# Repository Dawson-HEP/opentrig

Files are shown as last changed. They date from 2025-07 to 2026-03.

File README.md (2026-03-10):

# opentrig

> ***open***-source ***trig***ger system

An open-source, integrated, particle physics data acquisition system (DAQ).

Designed to interface with timing systems controlled by the [AIDA-2020 TLU](https://gitlab.com/ohwr/project/fmc-mtlu).
Up to 24 digital trigger channels with variable-gain threshold setting.

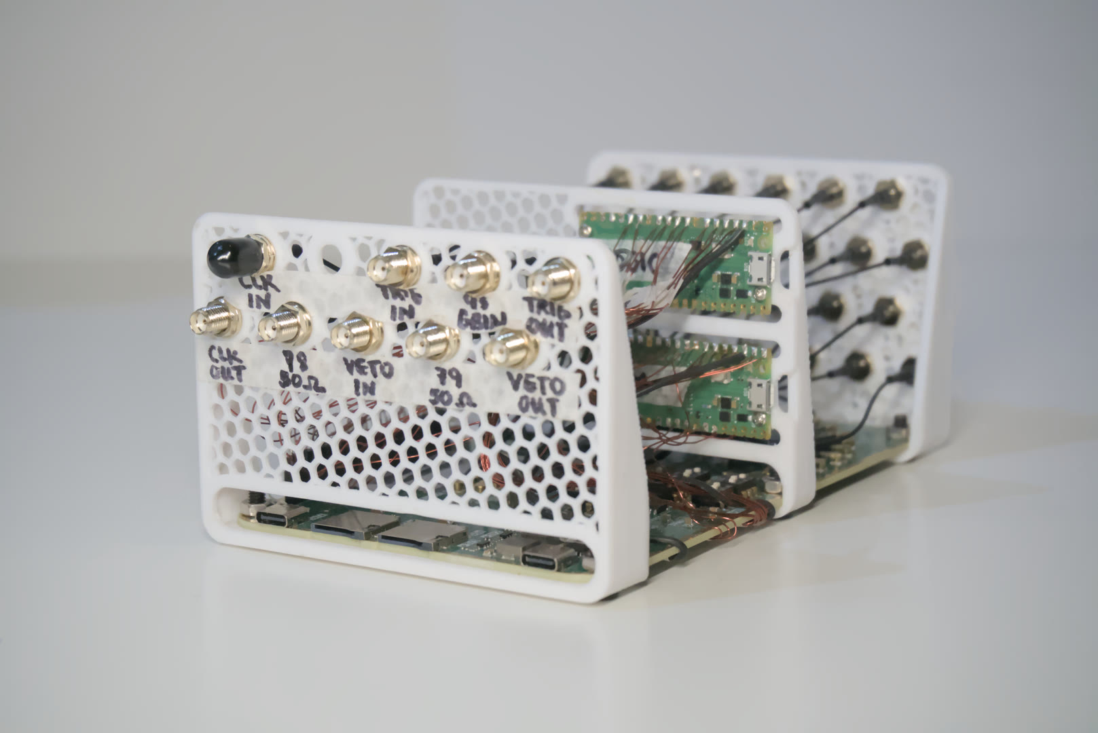
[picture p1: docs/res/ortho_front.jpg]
Main picture of opentrig


## Features

- 144 MHz internal FPGA clock, and timing resolution
- 24 digital trigger channels with variable gain
- Input voltage range 3.3V-5V
- TTL level compatible clock, trigger, input and output
- [AIDA-2020 TLU synchronous AIDA mode](https://gitlab.com/ohwr/project/fmc-mtlu/-/raw/master/Documentation/Main_TLU.pdf?ref_type=heads) (page 31) compatible FPGA

## Hardware Overview

[**Schematics can be found here.**](hardware/digital.pdf)

Front panel IO (left)
- Input clock signal (<40 MHz square wave)
- Output clock signal (120 MHz square wave, 3.3V TTL, <0.5% jitter, phase-locked)
- Input/output trigger (3.3V TTL)
- Input/output veto (3.3V TTL)
- Extra 50R impedance-matched inputs

Back panel (right)
- 24 channel digital inputs, with variable trigger thresholds (1.024 mV steps):
    - 0.000V-2.000V (1x gain)
    - 0.000V-4.000V (2x gain)

Internal components
- Low drift 5.000V reference (TI REF5050AIR)
- 12 high-speed thresholding comparators (TI TLV3502)
- 120 MHz MCU (RP2040)
- FPGA (Lattice ICE40 HX4K)

<p align="center">
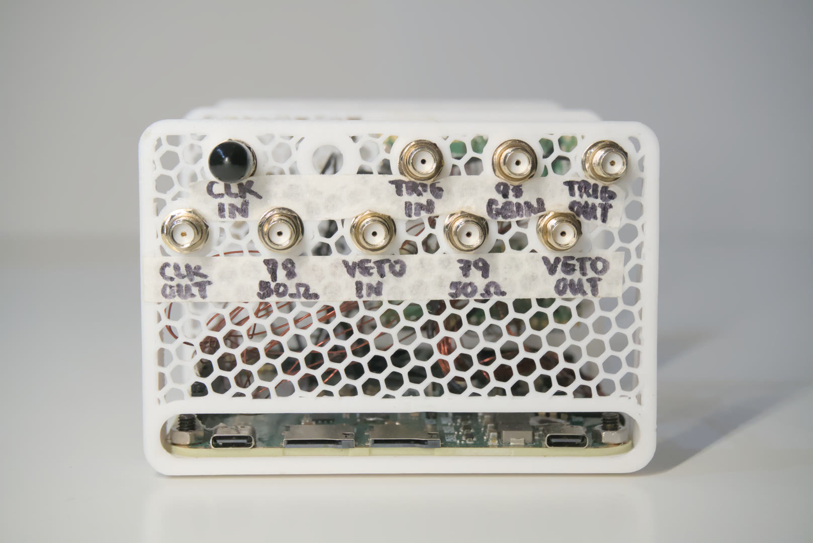
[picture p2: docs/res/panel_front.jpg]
Front panel
  
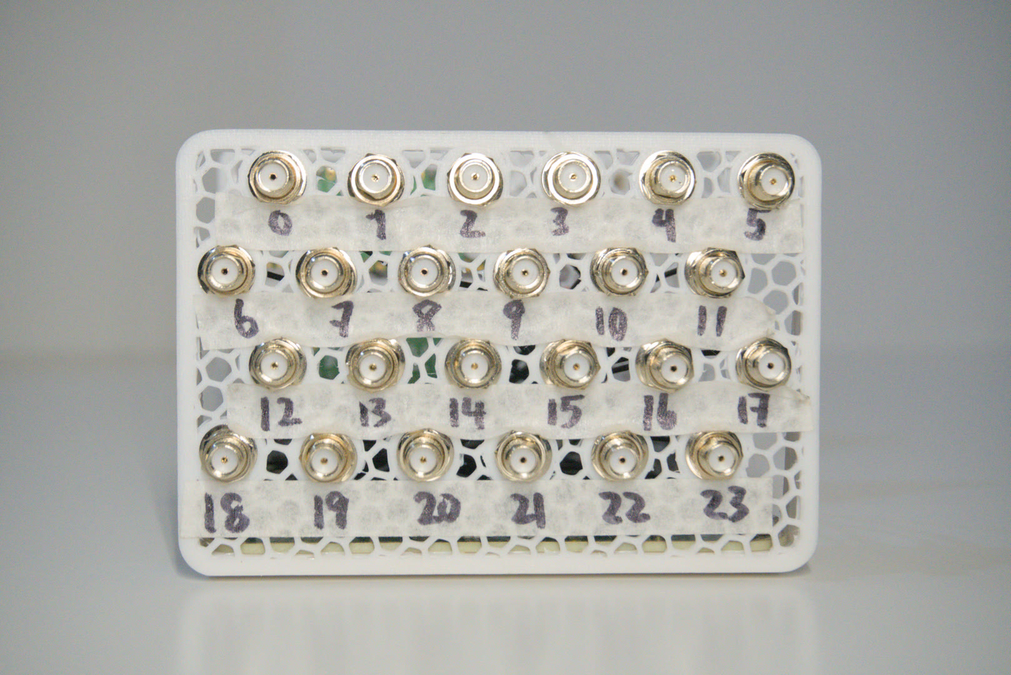
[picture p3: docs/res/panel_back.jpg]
Back panel
  
</p>

## Trigger Architecture

The *opentrig* system is a 24-channel, synchronous data acquisition platform compatible with EUDAQ2-compatible beamline trigger systems. Each channel digitizes an analog falling-edge into a digital rising-edge depending on a threshold set by independent digital-to-analog converters (DACs). Three trigger sources are fed into a selectable OR-ing gate, which allows for the selection of the interrupt source(s) for sample recording.

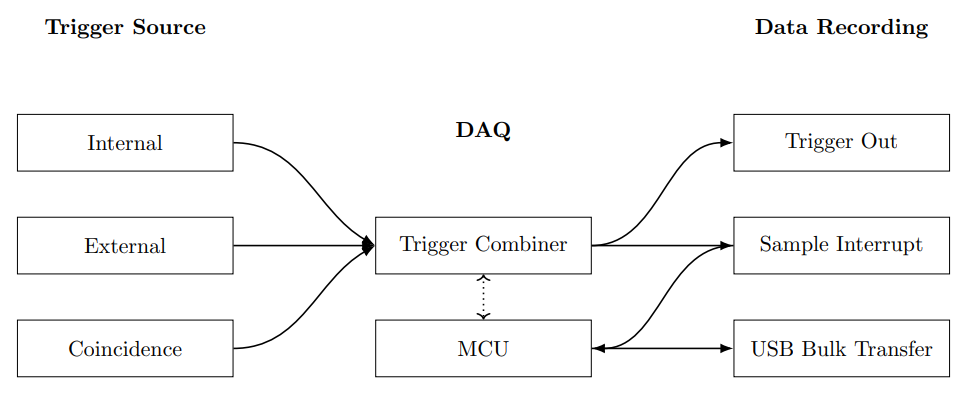
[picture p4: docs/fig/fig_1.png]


The trigger combiner vetoes priority in regards to the inputs of selected trigger sources, and assigns FPGA SPI bandwidth to the microcontroller (MCU) for processing and sampling. An active-high trigger output is asserted with controllable duration and delay in reference to the trigger sources. The sample interrupt interacts with the MCU in order to stream data live through the USB Type-C interface across bulk transfer.

### Trigger Delay

The delays incurred by the trigger is synchronized across channels by means of length matching. The largest skew is a result of level shifting: indeed up to $\pm 0.3$ ns across channels. No significant differences are measured in practice. FPGA gate skew is below the delays of level shifting, and are thus negligible in practice. PCB traces are delay-matched to within $\pm0.01$ mm. Given the assumption that channels are synchronized between each other, the input-output delay needs to be considered.

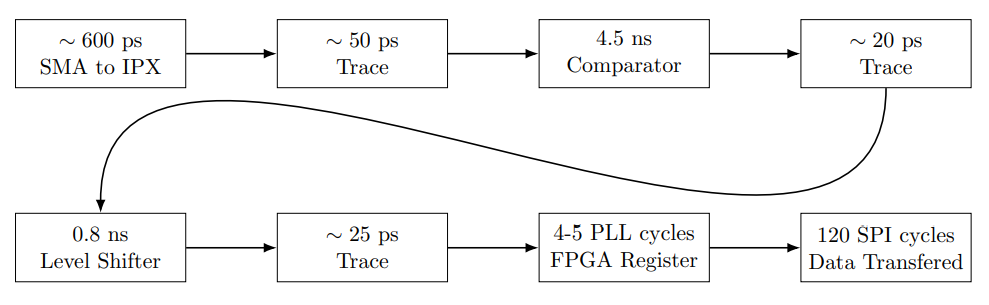
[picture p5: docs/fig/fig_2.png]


## Clocks

The FPGA PLL is synchronized to a sampling clock of $120$ MHz, while the SPI clock transfers data at a rate of $5$ MHz. The user can select an internal clock input or an external clock input, both requiring different PLL clock dividers to achieve the full sampling rate at $120$ Msps.

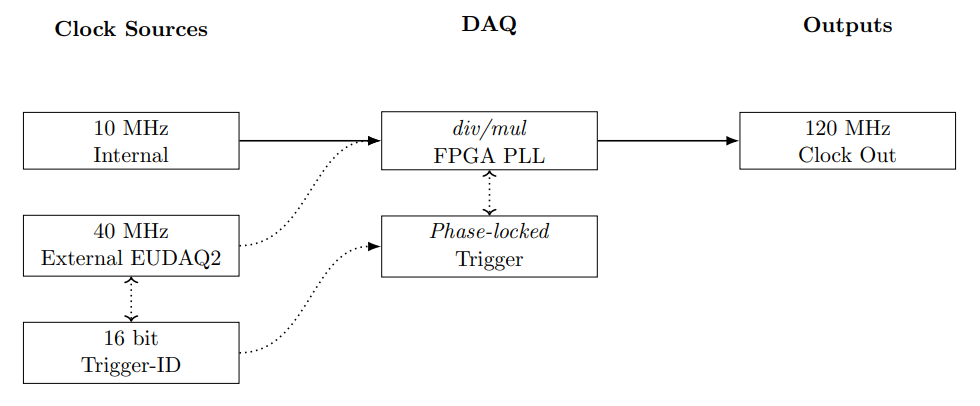
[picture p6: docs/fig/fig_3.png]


Clocks are phase-aligned by phase-locked-loop (PLL). An internal clock can be generated for the independent functioning of the DAQ. Proper PLL clock dividers and multipliers must be set to achieve the target $120$ MHz. An external clock compliant to EUDAQ2 trigger systems, such as the AIDA-2020 TLU, can be synchronized to \textit{opentrig}. A 16-bit trigger-ID can be read synchronously by the phase-locked external trigger module, which will be recorded upon the assertion of a sample interrupt.

## Voltage Levels

The 24 analog inputs are limited to a voltage range of $-0.30$ V to $+5.30$ V on wide-gain mode, and $-0.30$ V to $+3.30$ V on limited-gain mode. A voltage beyond permissible levels may cause irreversible damage to thresholding comparators, whose inputs are directly connected to SMA connectors.

The digital signals are high-impedance or $50 \Omega$ terminated depending on the label, and function on $3.3$ V CMOS voltage levels. The push-pull drivers have weak drive capabilities; therefore, only small digital loads may be attached with matched impedance.

## Directory Structure

The hardware is designed in [KiCad](https://www.kicad.org/) for the digital trigger front-end and mechanical layout, while the firmware and control utilities are written in [Rust](https://rust-lang.org/) using the [Embassy](https://embassy.dev/) embedded framework. The FPGA subsystems are written in pure Verilog with the [Yosys](https://github.com/YosysHQ/yosys.git) open-source toolchain, and [Project Icestorm](https://github.com/YosysHQ/icestorm)'s bitstream documentation.

```
opentrig/
├── hardware/ # KiCad hardware design
│   ├── fab/ # Fabrication files and gerbers
│   ├── logos.pretty/ # Custom logo footprints and graphics
│   └── digital.pretty/ # Custom digital footprints and component libraries
│
├── opentrig/ # Core DAQ firmware
│   ├── src/ # Source code (Rust + Embassy)
│   │   └── fpga/ # FPGA interface and logic modules
│   └── target/ # Compiled firmware output and build artifacts
│
├── cli/ # Command-line interface for control and configuration via host computer
│   ├── src/ # Rust source for CLI utilities
│   └── target/ # Compiled CLI binaries
│
├── tests/ # Automated and hardware-in-the-loop test framework
│   ├── src/ # Unit and integration test sources
│   └── target/ # Compiled test binaries and reports
│
└── README.md # Project overview, setup, and usage instructions
```

## Building

Before building the firmware and FPGA bitstream, you need to install a few dependencies for Rust and the FPGA toolchain. Follow these steps:

- Install [Rust](https://www.rust-lang.org/) – the firmware is written in Rust using the Embassy framework.
- Install [Just](https://github.com/casey/just) – used to run the build commands.
- Install [Yosys](https://github.com/YosysHQ/yosys) – for Verilog synthesis of the FPGA.
- Install [Project Icestorm](https://github.com/YosysHQ/icestorm) tools – for routing and bitstream generation for iCE40 FPGAs.
- Optional: [KiCad](https://www.kicad.org/) – for viewing and editing hardware schematics.

Once dependencies are installed, clone the repository, navigate to the firmware folder, and run the build commands:

```bash
# Clone the Protovolt repository from GitHub
git clone https://github.com/Dawson-HEP/opentrig.git

# Go to firmware directory
cd opentrig/opentrig
```

```bash
# Compile verilog bitstream
just build-verilog

# Compile embedded firmware
just build-rust
```

Flashing:
- SWD debug port on the PCB
- USB flashing via data port

## Running the DAQ
A USB Type-C Power Delivery (PD) supply must be connected to the power connector to bias analog and digital circuitry. A $100$ W-capable supply with $20$V output is preferred to provide enough margin for buck converters and analog filtering supplies to function properly. A digital data cable links the data acquisition computer with the DAQ.

## Debugging the DAQ
Three SWD debug interfaces are made available to the user: the main *opentrig* MCU debug link, the simulation PICO link, and the logic analyzer PICO link. The MCU flash process includes the FPGA bitstream, which is written upon power up of the DAQ. The simulation PICO, when powered, produce triggers via the internal links directly to the FPGA, which allows for programmatic debugging. The logic analyzer serves as a bitstream debugger, where internal registers and wires can be sampled.

## DESY Test Beam

The interfacing with the AIDA-2020 TLU functionality has been verified at the [DESY II Test Beam facility](https://desy.de/index_eng.html) in September of 2025, as part of the [Beamline for Schools](https://beamlineforschools.cern/) Competition. 

*Testbeam Area 21, Translation Stage*
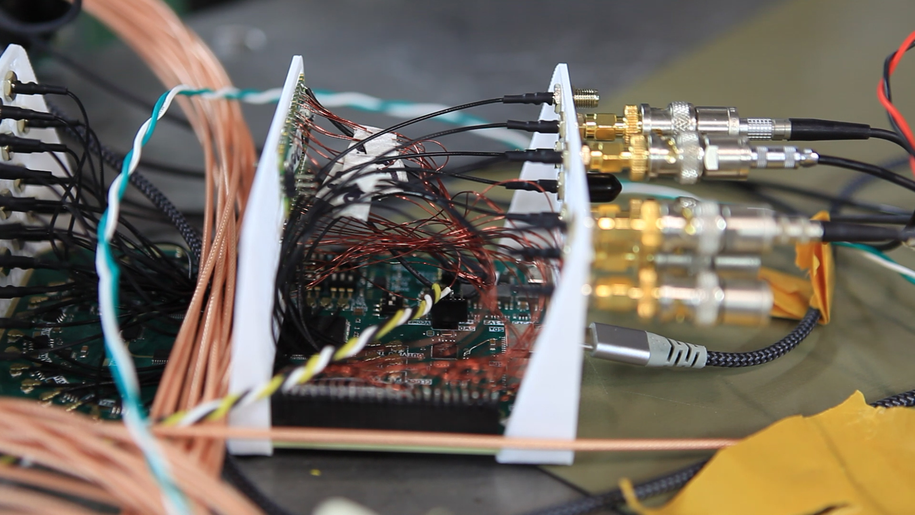
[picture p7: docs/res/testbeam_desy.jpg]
Testbeam


## Gallery

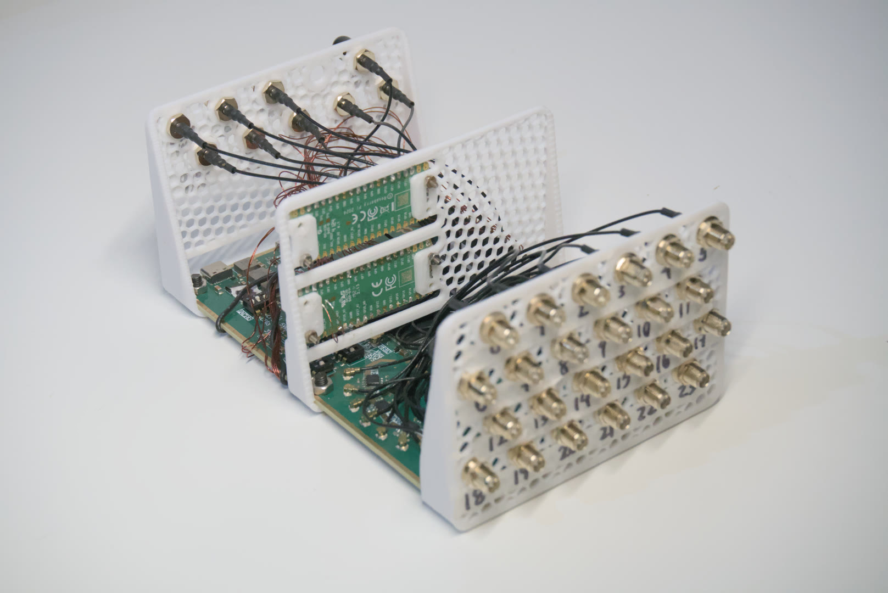
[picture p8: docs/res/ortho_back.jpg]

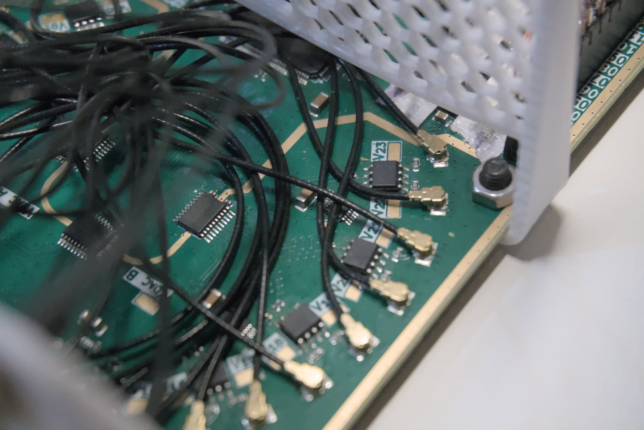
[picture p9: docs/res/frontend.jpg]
Frontend

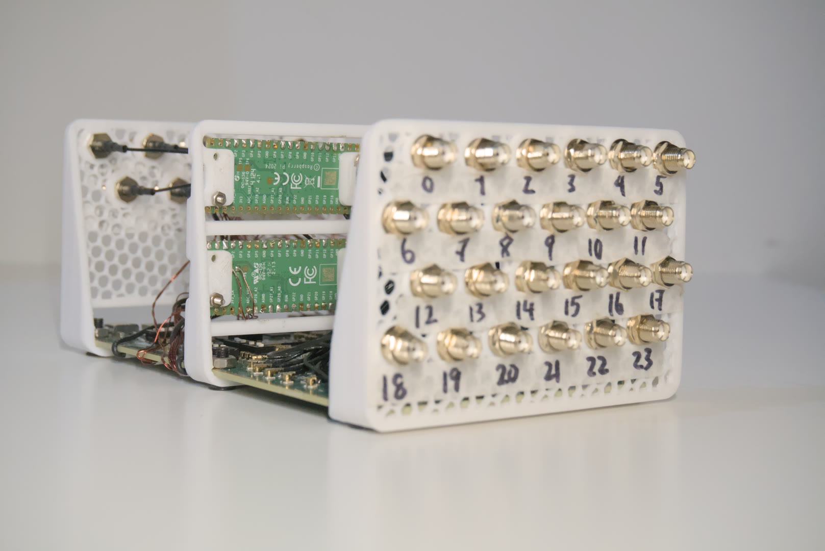
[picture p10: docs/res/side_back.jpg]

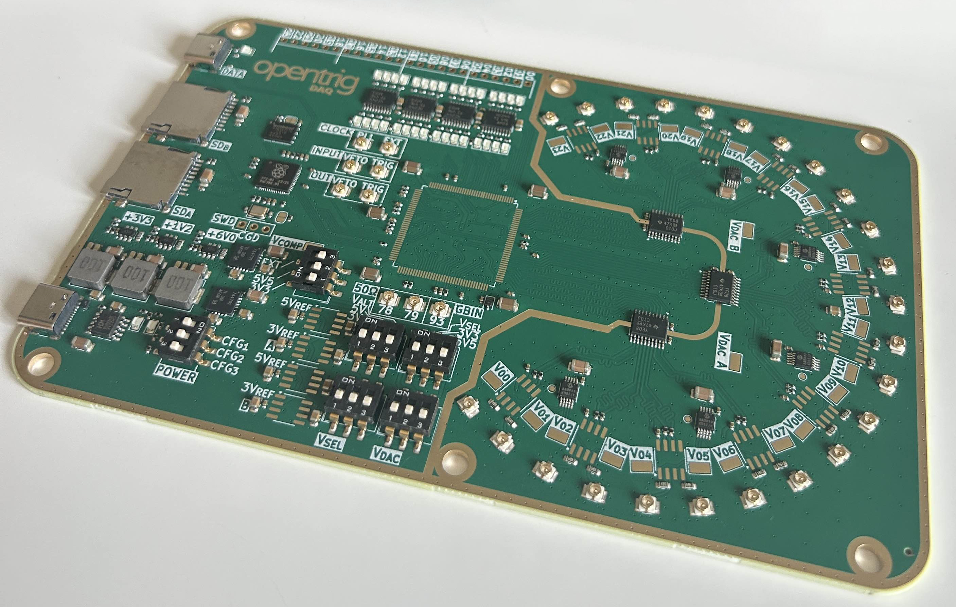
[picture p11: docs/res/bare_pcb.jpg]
Bare PCB


## License

This project is open-source under the Eclipse Public License - v 2.0.

## Authors

- [Tian Yi, Xia](https://github.com/ThatAquarel), xtxiatianyi@gmail.com
- [Leandro Perez-Moran](https://github.com/LudioRex), pemle2007@gmail.com

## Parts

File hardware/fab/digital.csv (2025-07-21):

Comment | Designator | Footprint | LCSC
100n | C1,C3,C4,C5,C6,C7,C8,C9,C11,C12,C13,C14,C15,C17,C19,C21,C22,C24,C25,C26,C27,C28,C29,C30,C31,C32,C36,C38,C41,C43,C51,C55,C59,C61,C69,C71,C73,C74,C77,C80,C81,C85,C86,C89,C92,C93,C97,C98,C99,C100,C101,C102,C103,C104,C105,C106,C107,C108,C109,C110,C111,C113,C114,C115,C116 | Capacitor_SMD:C_0402_1005Metric | C307331
1u | C10,C47,C48,C52,C53,C66,C67,C68,C70,C72,C75,C78,C82,C83,C87,C90,C94,C95,C112 | Capacitor_SMD:C_0805_2012Metric | C28323
4.7u | C2,C16,C18,C20,C23 | Capacitor_SMD:C_1206_3216Metric | C29823
1u 25V | C33,C34 | Capacitor_SMD:C_0402_1005Metric | C52923
10u | C35,C37,C42,C49,C50,C54,C60,C65,C76,C79,C84,C88,C91,C96 | Capacitor_SMD:C_1206_3216Metric | C13585
15p | C39,C40 | Capacitor_SMD:C_0402_1005Metric | C1548
100p | C44 | Capacitor_SMD:C_0402_1005Metric | C1546
22u | C45,C46,C57,C58,C63,C64 | Capacitor_SMD:C_0603_1608Metric | C60077
47p | C56,C62 | Capacitor_SMD:C_0402_1005Metric | C1567
LED | D1,D2,D3,D4,D5,D6,D8,D9,D11,D12,D13,D14,D15,D16,D17,D18,D19,D20,D21,D22,D23,D24,D25,D26,D27,D28,D29,D30,D31,D32,D33,D34,D35,D36,D37 | LED_SMD:LED_0805_2012Metric | C2297
ESDA25P35 | D10 | digital:D_1610_4027Metric | C1974707
1N4148WS | D7 | Diode_SMD:D_SOD-323 | C2128
IPEX-1 | J1,J2,J3,J4,J5,J6,J7,J8,J9,J21,J22,J23,J24,J25,J26,J27,J28,J29,J30,J31,J32,J33,J34,J35,J36,J37,J38,J39,J40,J41,J42,J43,J44 | digital:BWIPX-1-001E | C496552
Conn_01x03_Pin | J10,J11,J13,J15 | Connector_PinHeader_1.00mm:PinHeader_1x03_P1.00mm_Vertical_SMD_Pin1Left
Conn_01x10_Pin | J12 | Connector_PinHeader_1.00mm:PinHeader_1x10_P1.00mm_Vertical_SMD_Pin1Left
Conn_01x02_Pin | J14 | Connector_PinHeader_1.00mm:PinHeader_1x02_P1.00mm_Vertical_SMD_Pin1Left
Micro_SD_Card_Det1 | J16,J18 | digital:microSD_HC_MSD-4-A | C91145
Conn_01x03_Pin | J17 | Connector_PinHeader_2.54mm:PinHeader_1x03_P2.54mm_Vertical
USB_C_Receptacle_USB2.0_16P | J19,J20 | Connector_USB:USB_C_Receptacle_GCT_USB4105-xx-A_16P_TopMnt_Horizontal | C165948
Conn_01x24_Pin | J45 | Connector_PinHeader_2.54mm:PinHeader_1x24_P2.54mm_Vertical
10uH | L1,L2,L3 | Inductor_SMD:L_Changjiang_FXL0630 | C167223
49.9R | R1,R2 | Resistor_SMD:R_0402_1005Metric | C25120
470R | R10,R11,R12,R13,R14,R15,R16,R18,R58,R61,R62,R63,R64,R65,R66,R67,R68,R70,R71,R72,R73,R74,R75,R76,R77,R80,R81,R82,R83,R84,R85,R86,R87 | Resistor_SMD:R_0402_1005Metric | C25117
100R | R17 | Resistor_SMD:R_0402_1005Metric | C25076
10k | R21,R28,R29,R30,R31,R32,R34,R35,R48,R51,R55,R56,R57 | Resistor_SMD:R_0402_1005Metric | C25744
4.7k | R22,R23 | Resistor_SMD:R_0402_1005Metric | C25900
1k | R24,R27,R37,R50,R52,R54 | Resistor_SMD:R_0402_1005Metric | C11702
27R | R25,R26 | Resistor_SMD:R_0402_1005Metric | C138021
0R | R3,R4,R5,R6,R7,R8,R9,R19,R20,R33,R36,R69,R78,R88 | Resistor_SMD:R_0402_1005Metric | C17168
47k | R38,R40,R49 | Resistor_SMD:R_0402_1005Metric | C25792
100k | R39,R43 | Resistor_SMD:R_0603_1608Metric | C25803
33k | R41,R45 | Resistor_SMD:R_0402_1005Metric | C25779
100k | R42,R46 | Resistor_SMD:R_0402_1005Metric | C25741
22k | R44,R53 | Resistor_SMD:R_0402_1005Metric | C25768
220k | R47 | Resistor_SMD:R_0603_1608Metric | C22961
5.1k | R59,R60 | Resistor_SMD:R_0402_1005Metric | C25905
49.9R | R89,R90,R96,R97,R101,R102,R103,R104,R107,R108,R114,R115,R117,R118,R119,R120,R124,R125,R131,R132,R133,R134,R135,R136 | Resistor_SMD:R_0603_1608Metric | C23185
10R | R91,R92,R93,R94,R95,R98,R99,R100,R105,R106,R109,R110,R111,R112,R113,R116,R121,R122,R123,R126,R127,R128,R129,R130 | Resistor_SMD:R_0402_1005Metric | C25077
SW_DIP_x03 | SW1,SW2,SW3,SW4,SW5,SW6 | Button_Switch_SMD:SW_DIP_SPSTx03_Slide_6.7x9.18mm_W8.61mm_P2.54mm_LowProfile | C129079
TestPoint | TP1,TP2,TP3,TP5,TP6,TP11,TP14,TP16,TP18,TP23,TP25,TP27,TP31,TP34,TP36,TP38,TP43,TP45,TP46 | TestPoint:TestPoint_Pad_D1.0mm
TestPoint_Alt | TP4,TP7,TP8,TP9,TP10,TP12,TP13,TP15,TP17,TP19,TP20,TP21,TP22,TP24,TP26,TP28,TP29,TP30,TP32,TP33,TP35,TP37,TP39,TP40,TP41,TP42,TP44 | digital:TestPoint_Keystone_5015_Micro_Mini | C159868
ICE40HX4K-TQ144 | U1 | Package_QFP:TQFP-144_20x20mm_P0.5mm
CH224K | U10 | Package_SO:SSOP-10-1EP_3.9x4.9mm_P1mm_EP2.1x3.3mm | C970725
REF5030ID | U14,U19 | Package_SO:SOIC-8_3.9x4.9mm_P1.27mm | C2878155
MCP4728 | U15,U16,U18,U20,U21,U23 | Package_SO:MSOP-10_3x3mm_P0.5mm | C108207
REF5050ID | U17,U22 | Package_SO:SOIC-8_3.9x4.9mm_P1.27mm
74HC244 | U2,U11,U12,U13 | Package_SO:TSSOP-20_4.4x6.5mm_P0.65mm | C6835
TXB0108PW | U24,U29,U34 | Package_SO:TSSOP-20_4.4x6.5mm_P0.65mm | C53406
TLV3502AIDR | U25,U26,U27,U28,U30,U31,U32,U33,U35,U36,U37,U38 | Package_SO:SOIC-8_3.9x4.9mm_P1.27mm
W25Q32JVZP | U3 | Package_SON:WSON-8-1EP_6x5mm_P1.27mm_EP3.4x4.3mm | C571260
RP2040 | U4 | Package_DFN_QFN:QFN-56-1EP_7x7mm_P0.4mm_EP3.2x3.2mm | C2040
TPS54302 | U5,U8,U9 | Package_TO_SOT_SMD:SOT-23-6 | C129370
TPS7A4701 | U6,U7 | Package_DFN_QFN:Texas_RGW0020A_VQFN-20-1EP_5x5mm_P0.65mm_EP3.15x3.15mm_ThermalVias | C90084
12 MHz ABM8-272-T3 | Y1 | Crystal:Crystal_SMD_Abracon_ABM8AIG-4Pin_3.2x2.5mm | C20625731

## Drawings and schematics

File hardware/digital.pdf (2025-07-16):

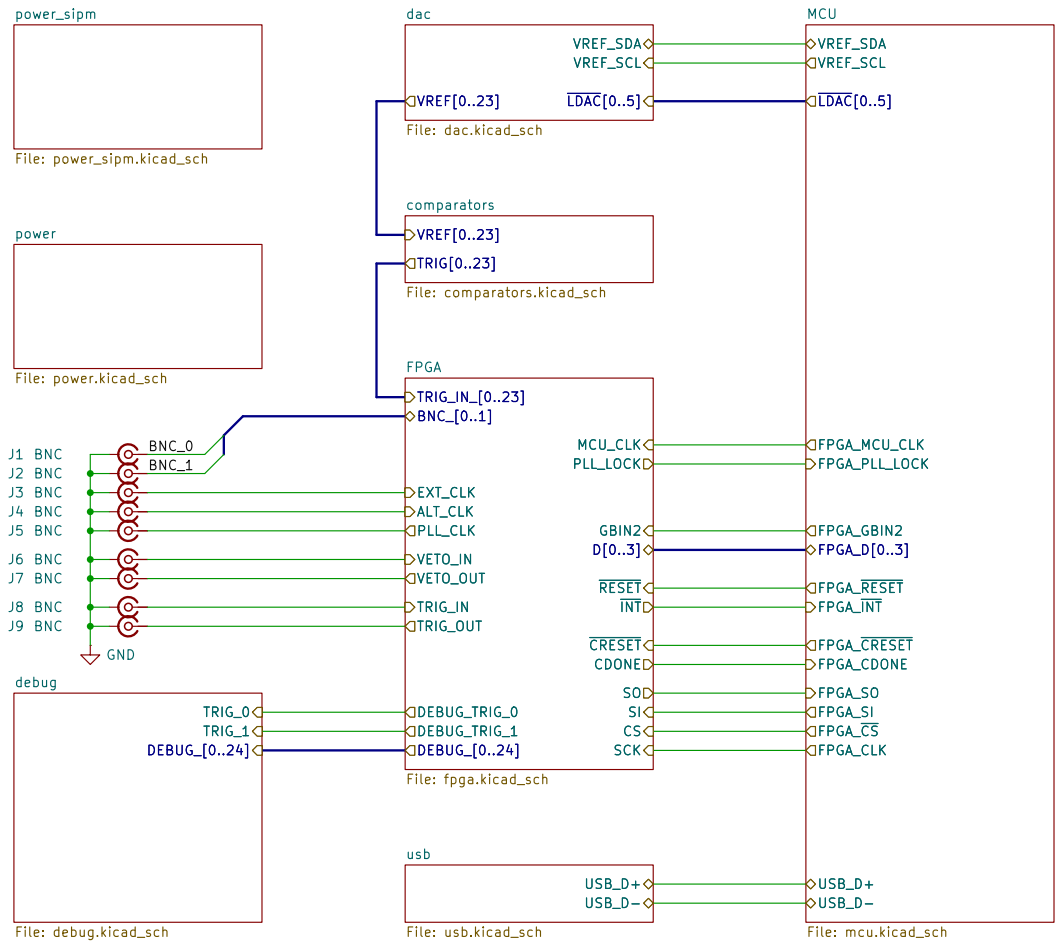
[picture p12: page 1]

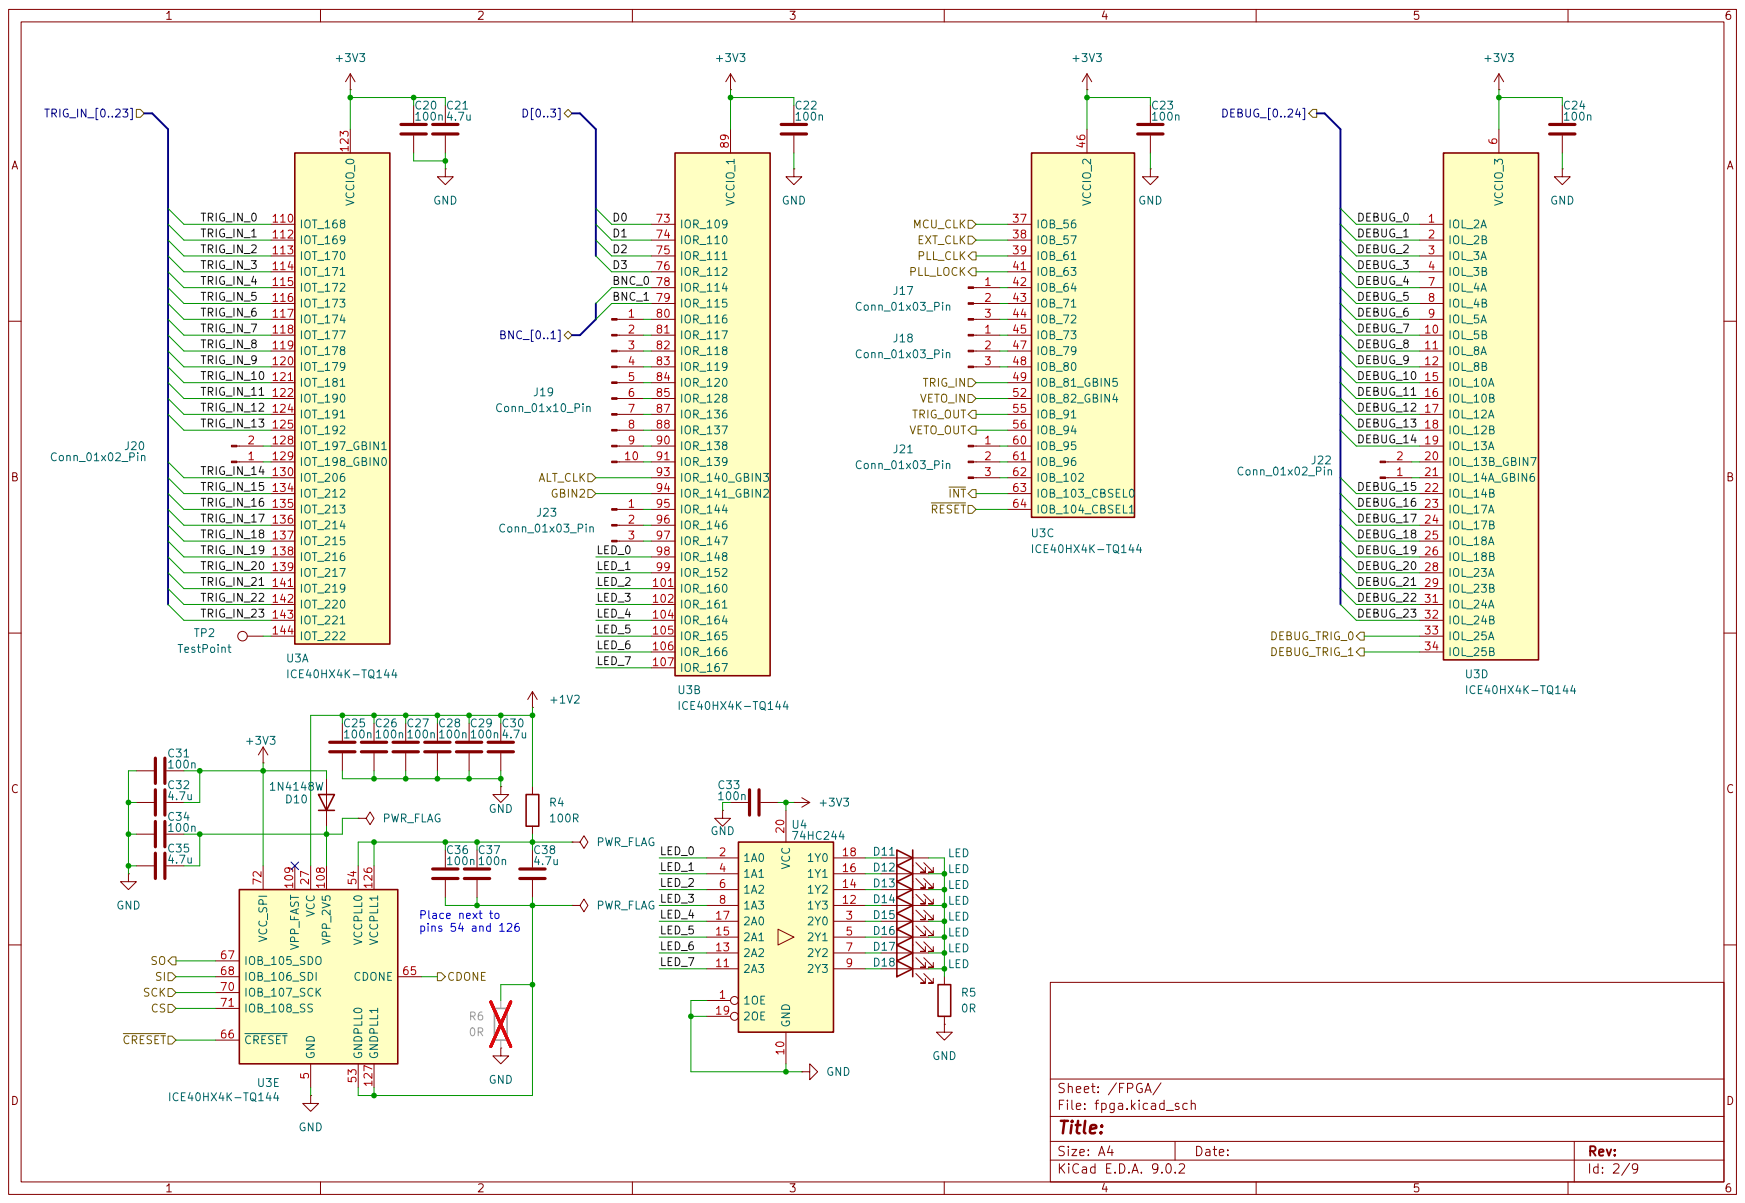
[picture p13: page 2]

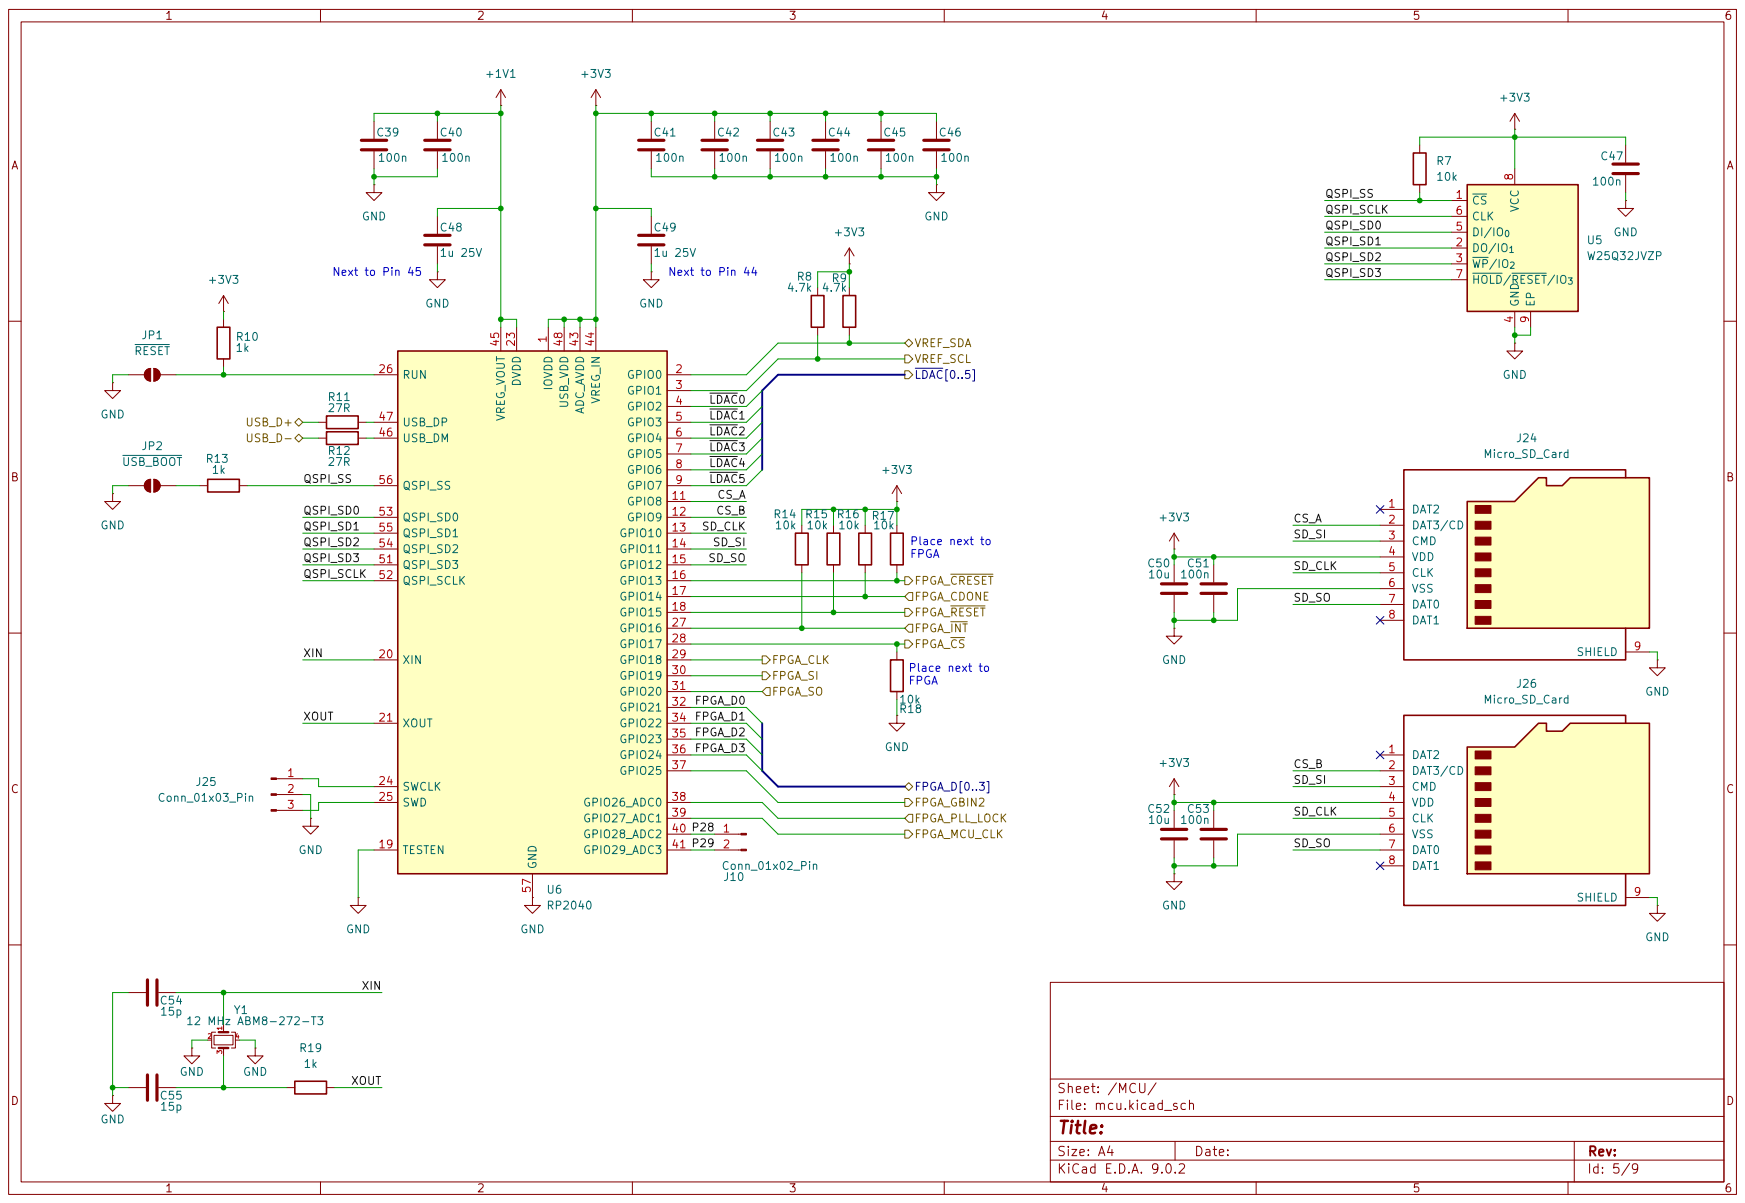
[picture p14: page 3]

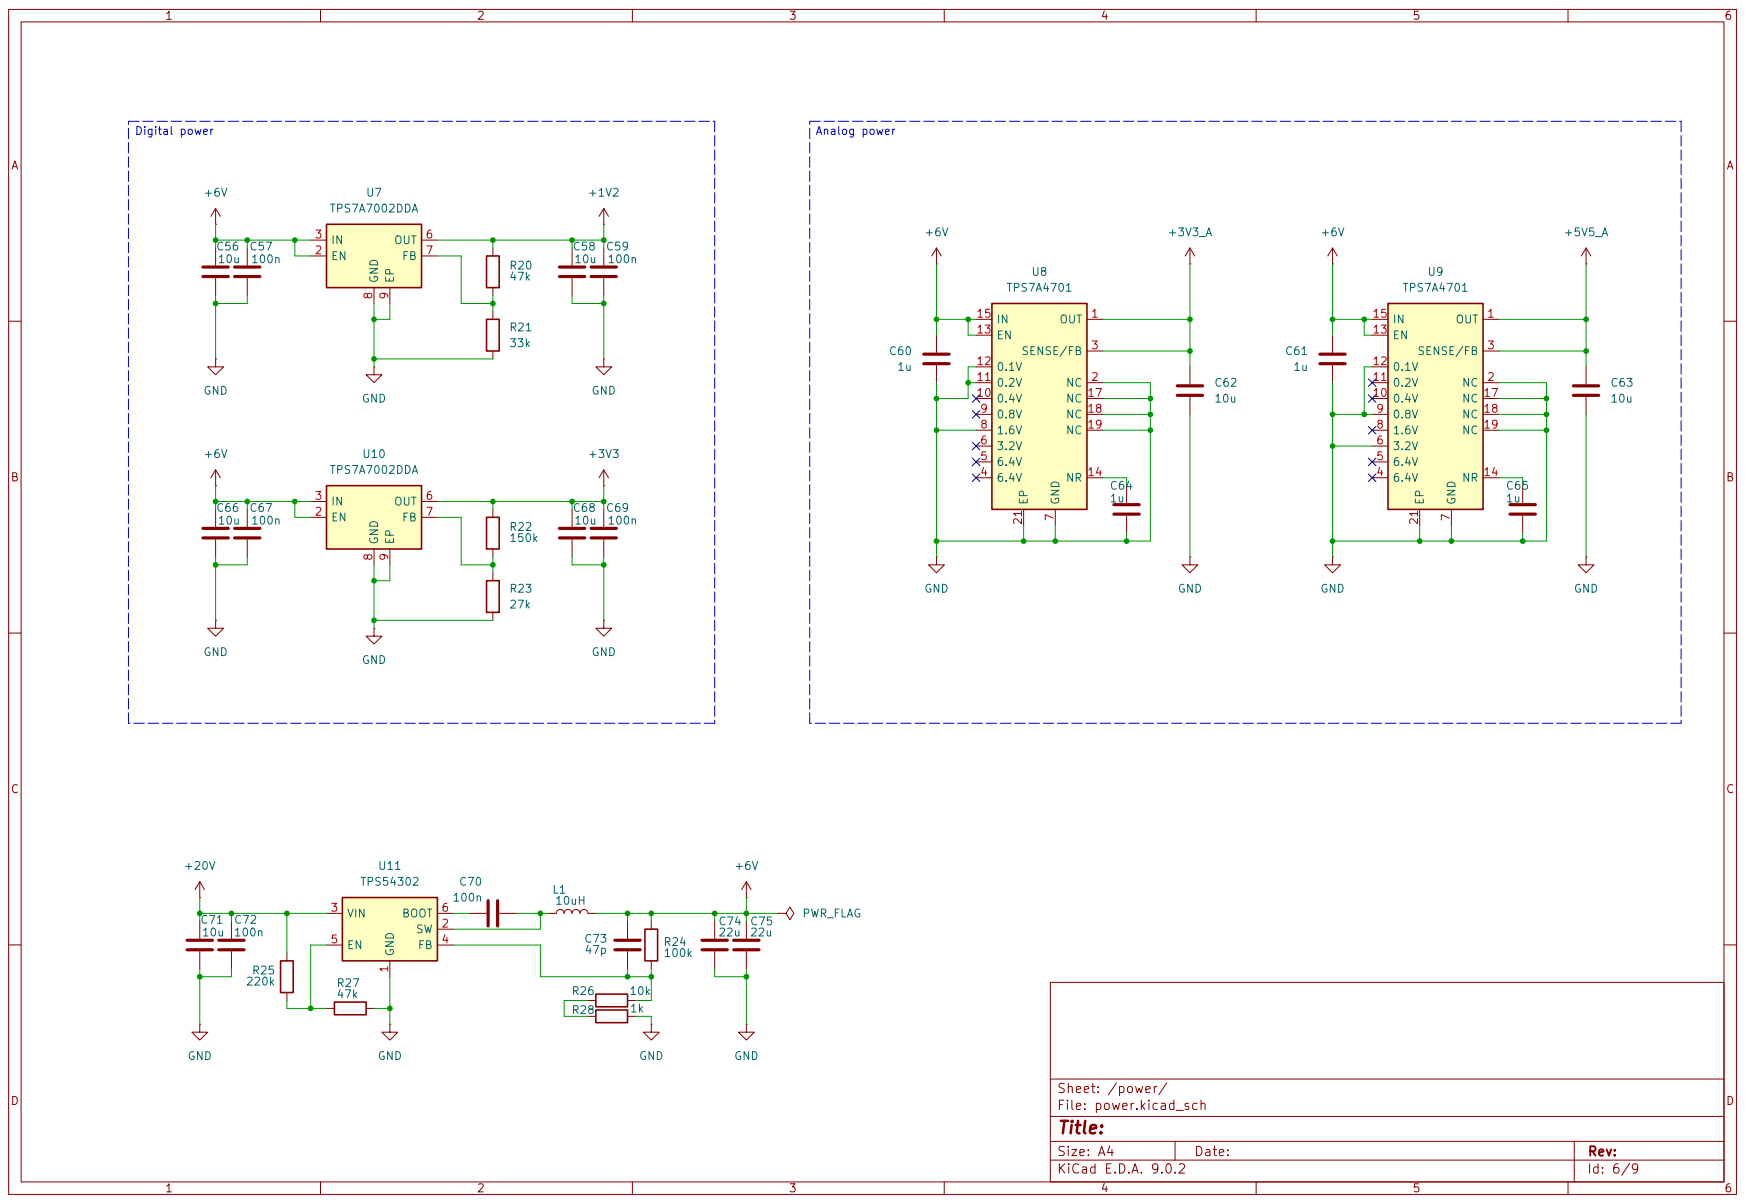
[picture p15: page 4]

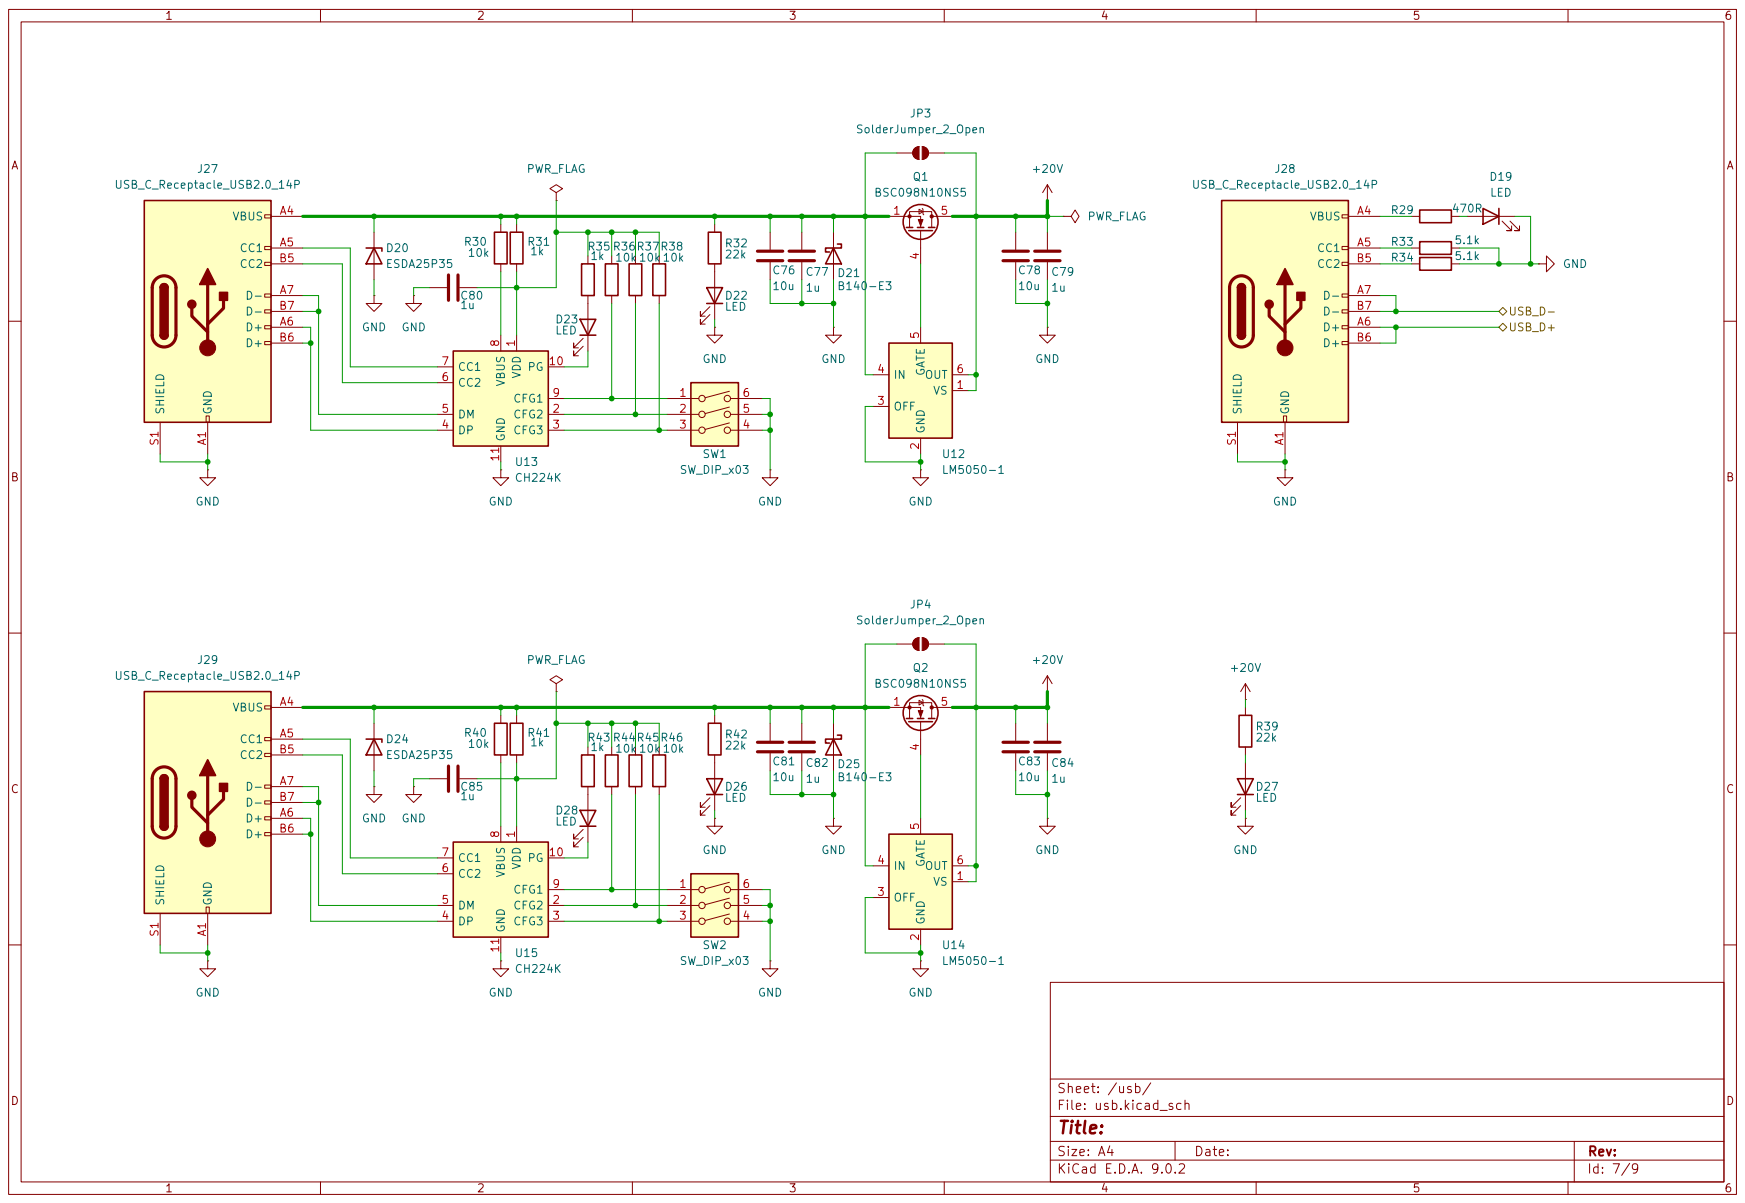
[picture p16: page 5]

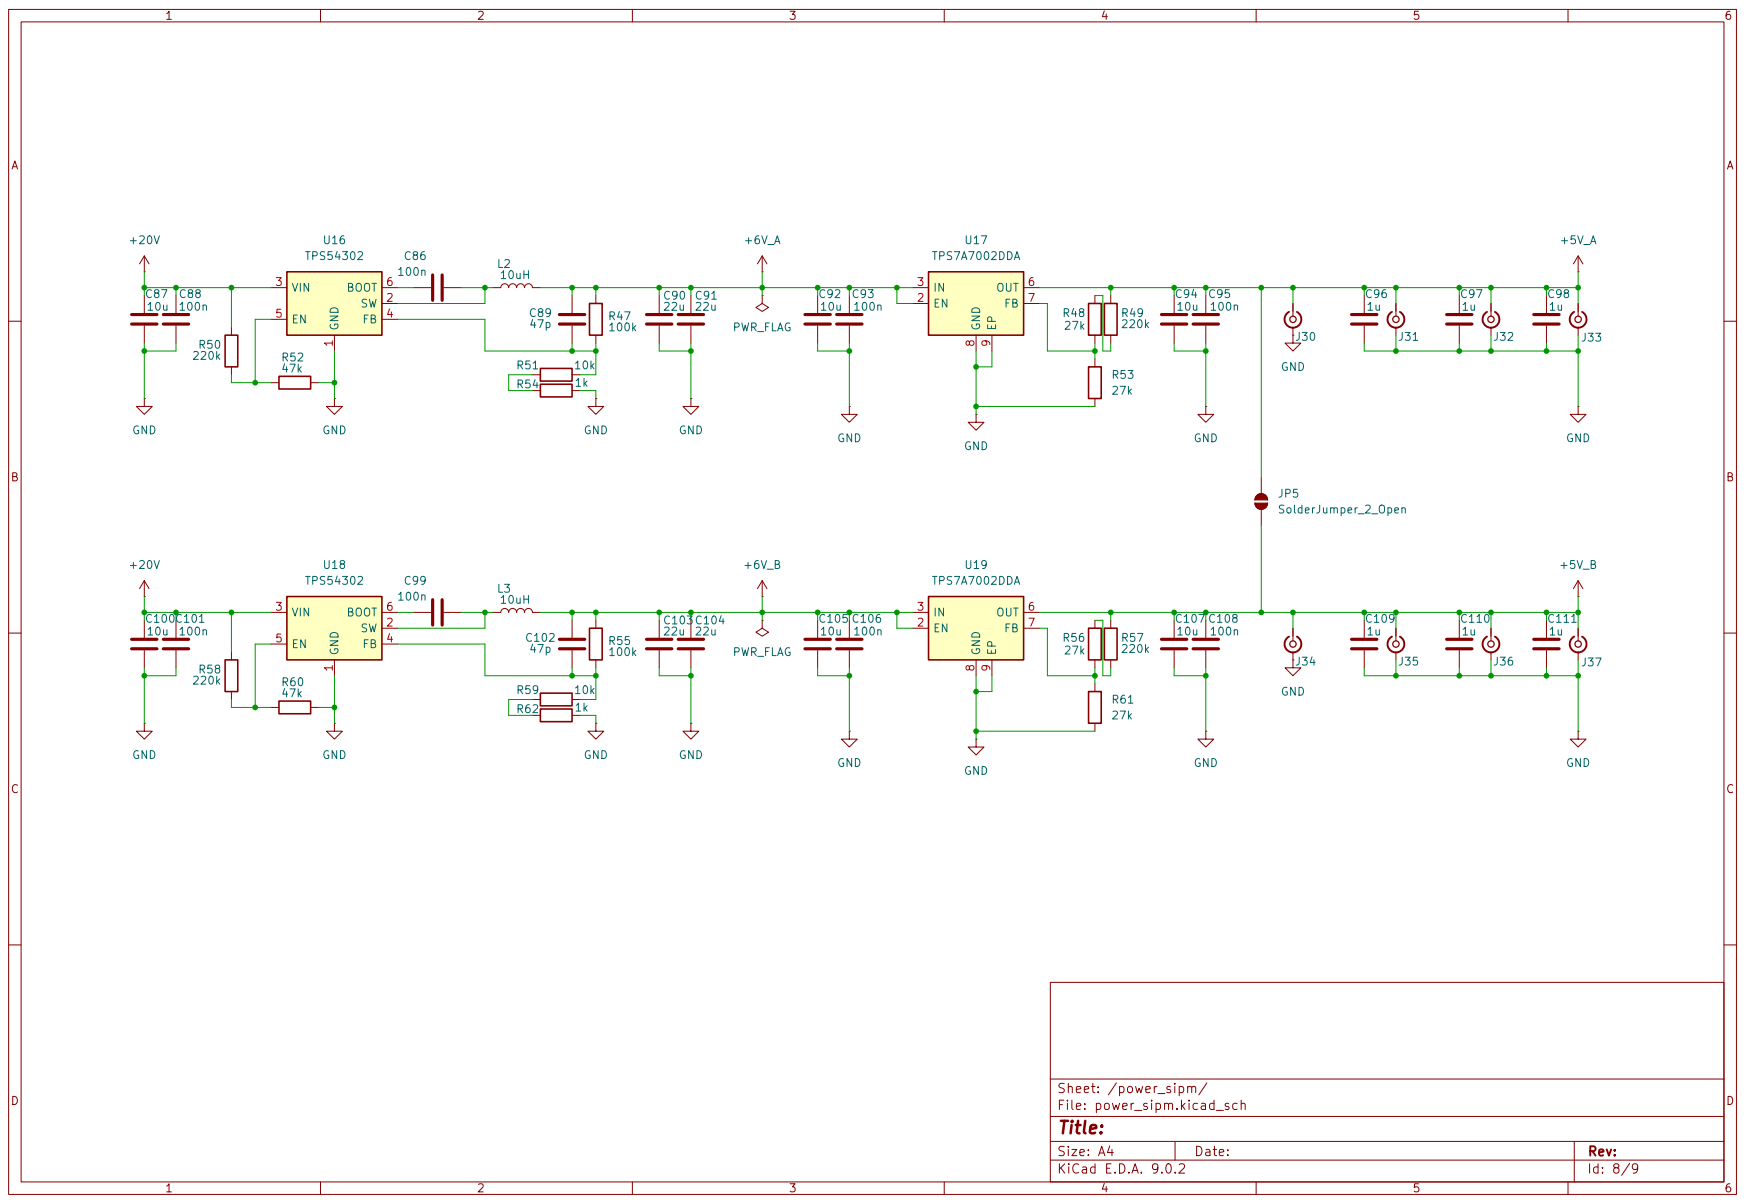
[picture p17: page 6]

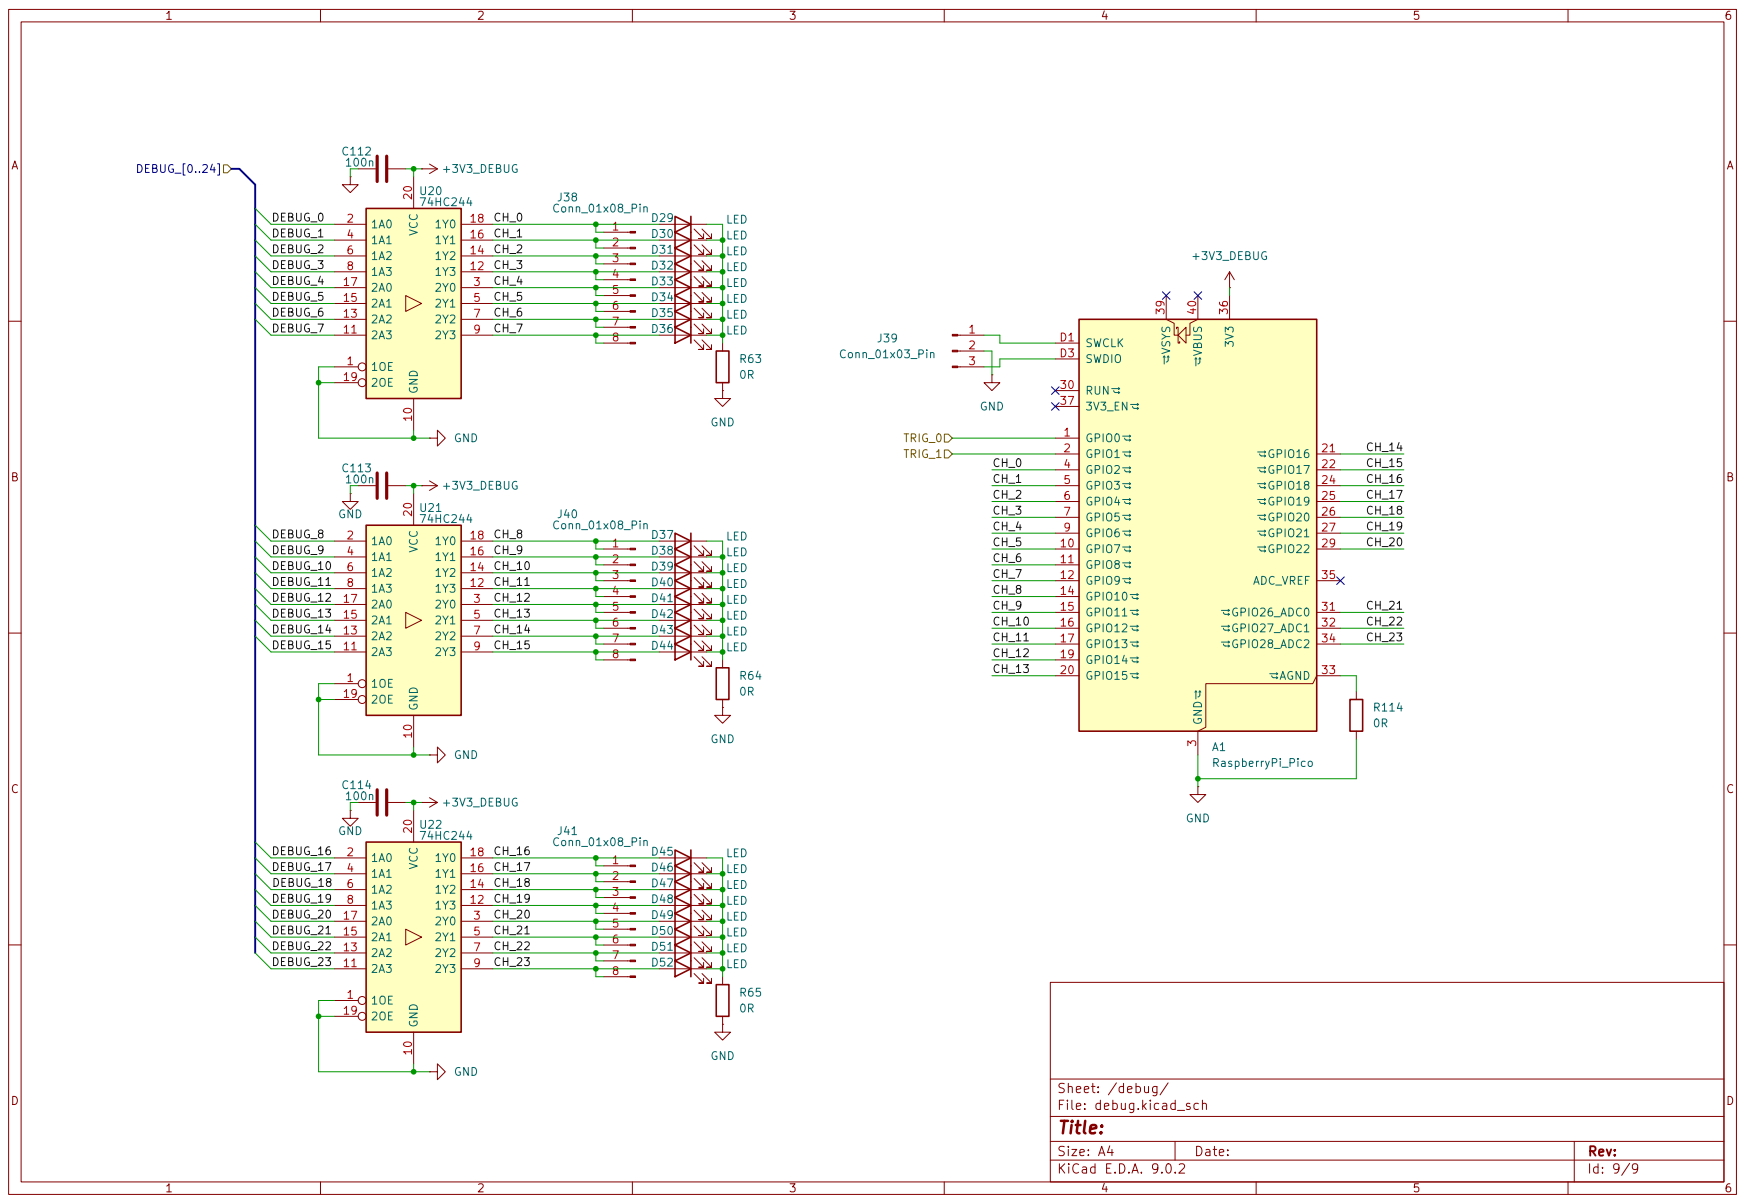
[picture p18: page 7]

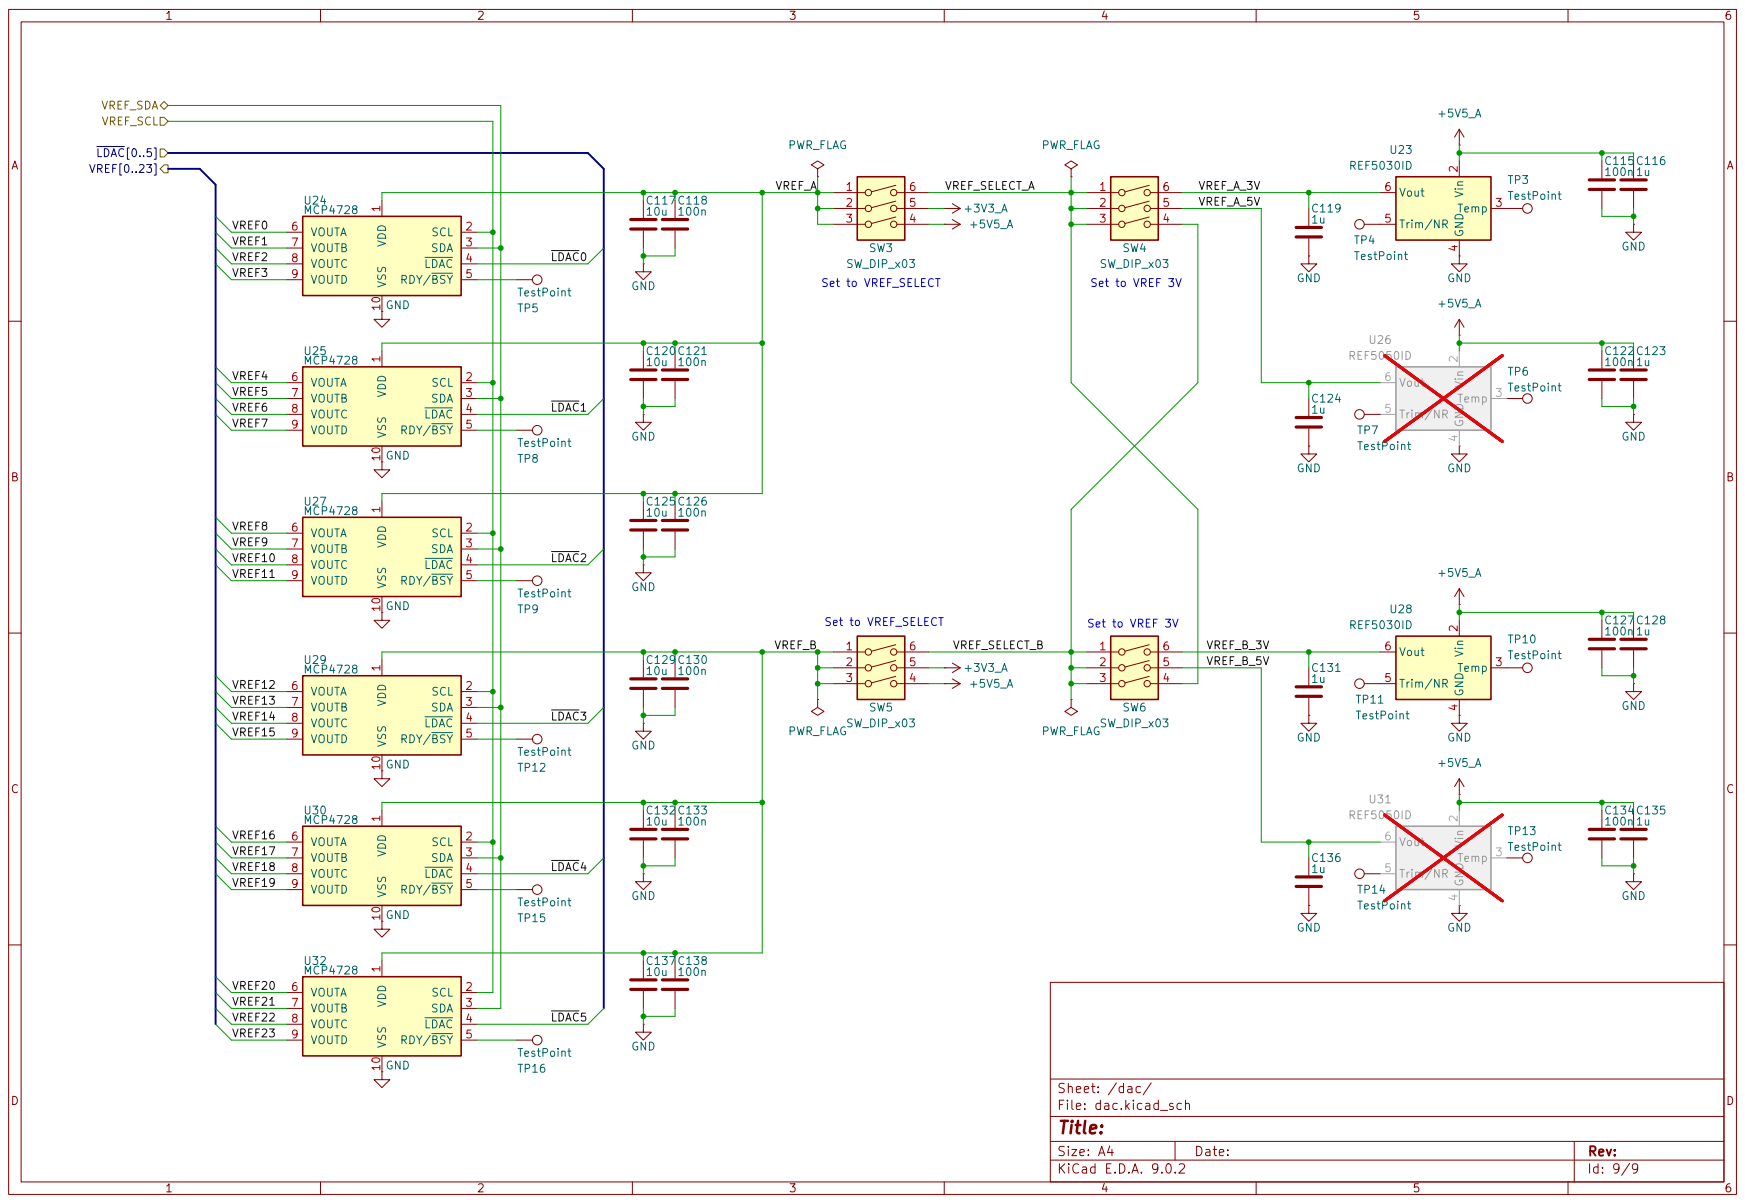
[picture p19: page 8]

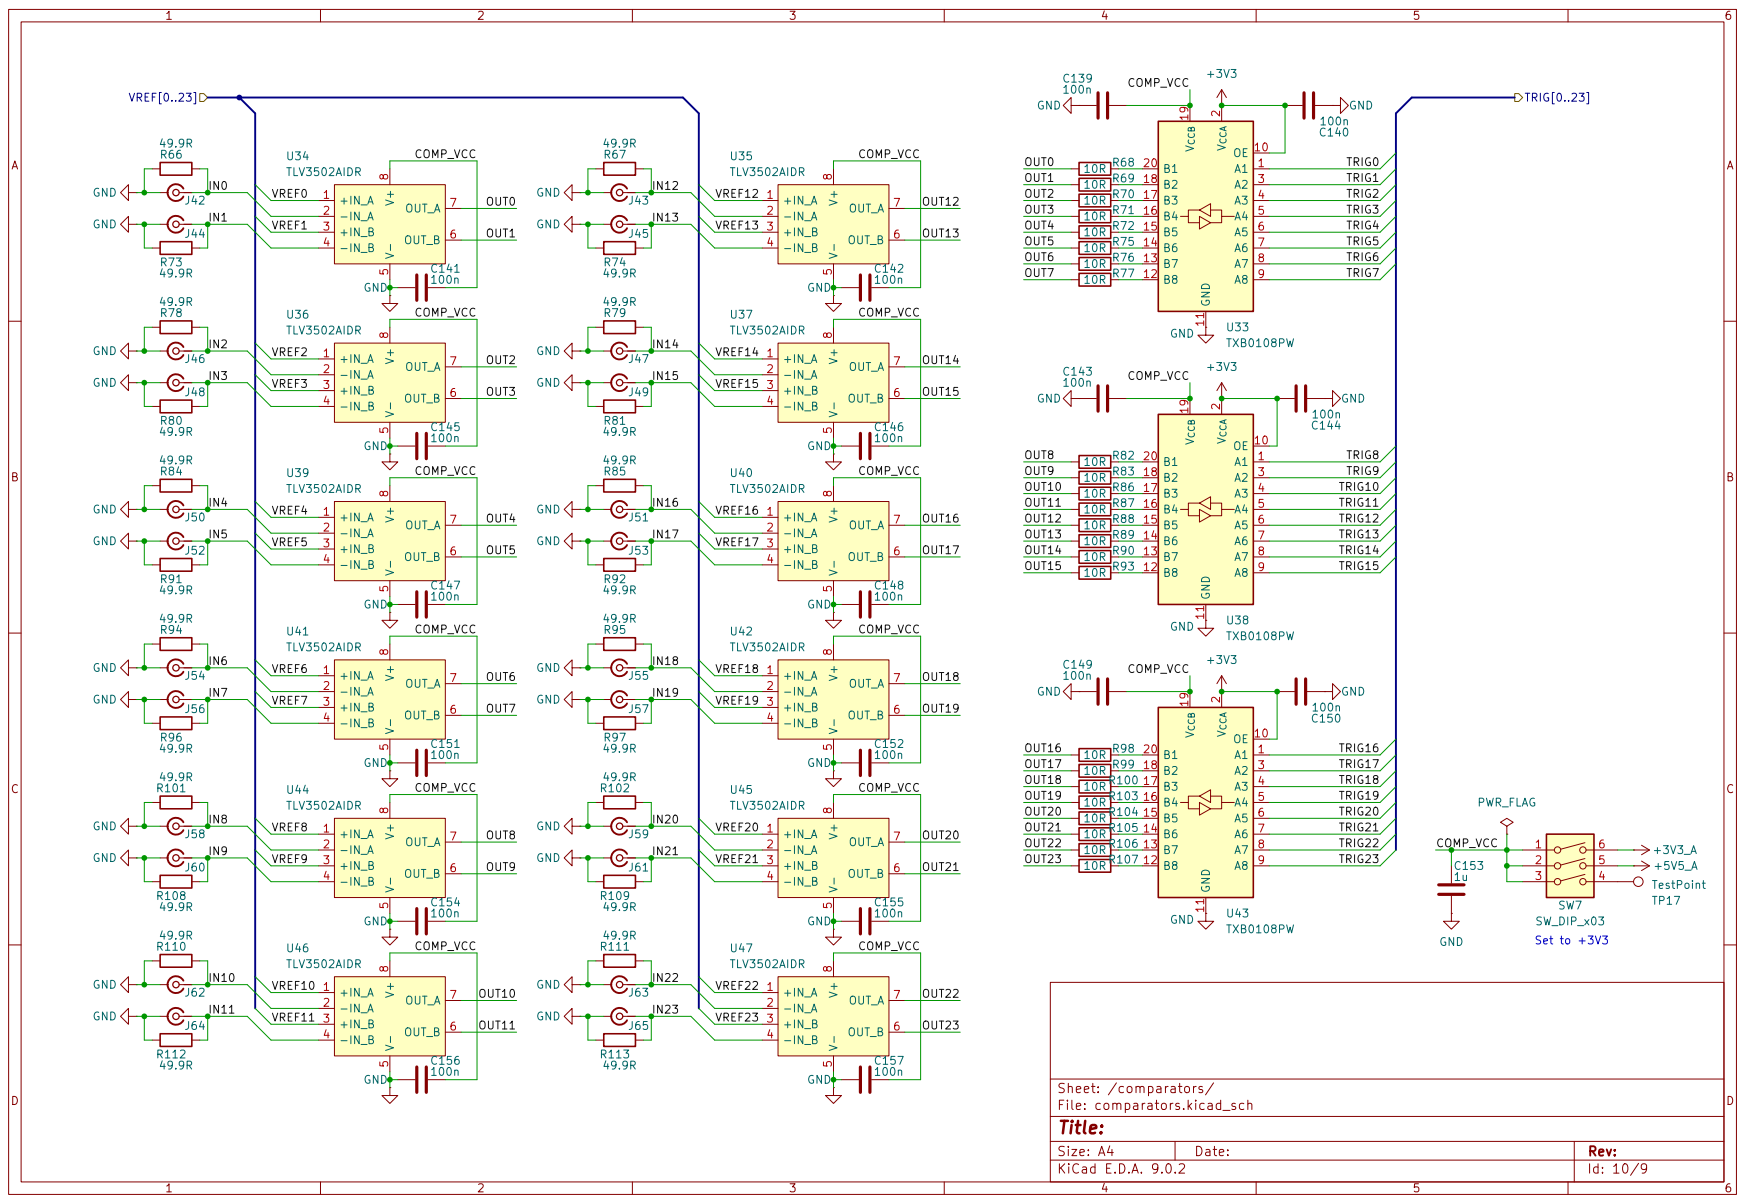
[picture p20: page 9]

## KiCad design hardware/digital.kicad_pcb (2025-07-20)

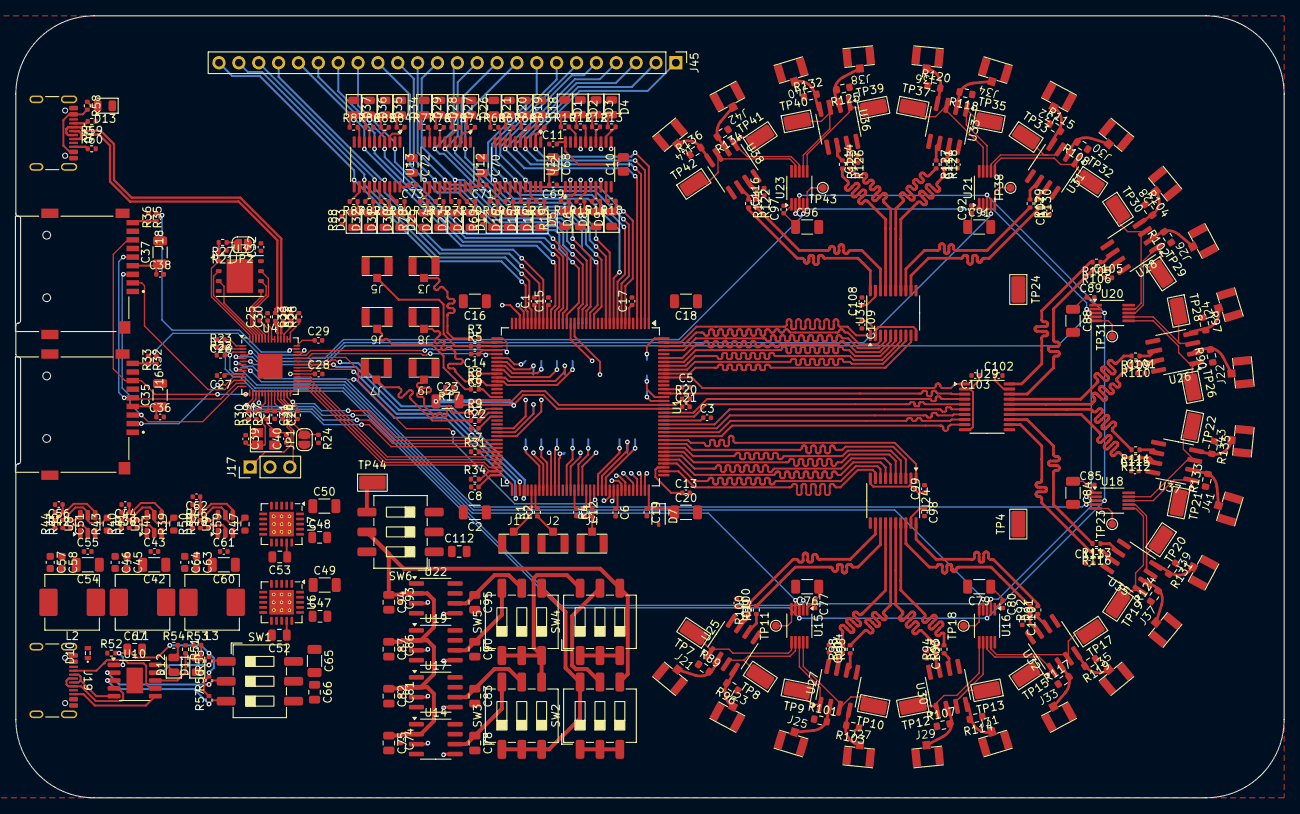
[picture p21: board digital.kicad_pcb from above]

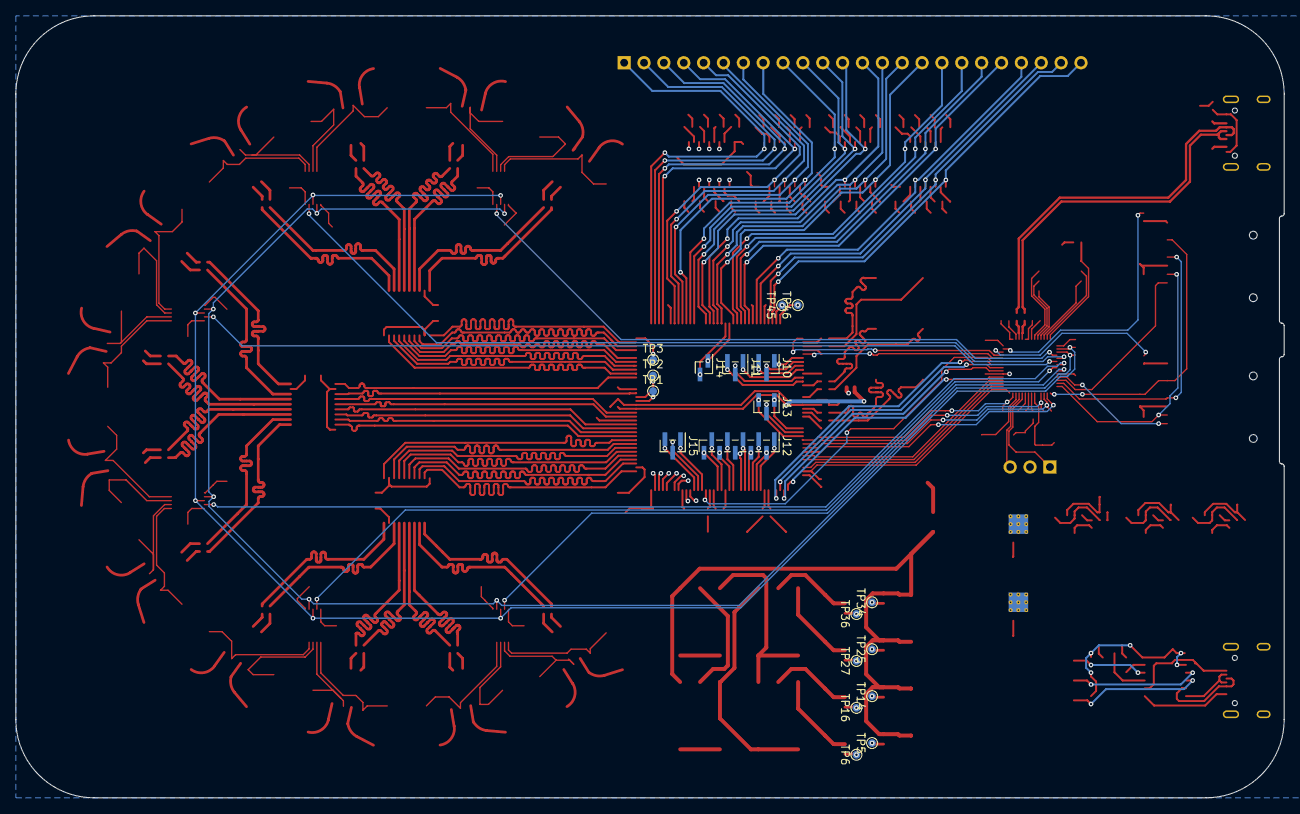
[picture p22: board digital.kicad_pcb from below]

Board: 4 copper layers, 162.2 x 100.0 mm, 429 parts (19 on the bottom side), 382 nets.

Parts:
C1, C3, C4, C5, C6, C7, C8, C9, C11, C12, C13, C14, C15, C17, C19, C21, C22, C24, C25, C26, C27, C28, C29, C30, C31, C32, C36, C38, C41, C43, C51, C55, C59, C61, C69, C71, C73, C74, C77, C80, C81, C85, C86, C89, C92, C93, C97, C98, C99, C100, C101, C102, C103, C104, C105, C106, C107, C108, C109, C110, C111, C113, C114, C115, C116: 100n; C_0402_1005Metric
C2, C16, C18, C20, C23: 4.7u; C_1206_3216Metric
C10, C47, C48, C52, C53, C66, C67, C68, C70, C72, C75, C78, C82, C83, C87, C90, C94, C95, C112: 1u; C_0805_2012Metric
C33, C34: 1u 25V; C_0402_1005Metric
C35, C37, C42, C49, C50, C54, C60, C65, C76, C79, C84, C88, C91, C96: 10u; C_1206_3216Metric
C39, C40: 15p; C_0402_1005Metric
C44: 100p; C_0402_1005Metric
C45, C46, C57, C58, C63, C64: 22u; C_0603_1608Metric
C56, C62: 47p; C_0402_1005Metric
D1, D2, D3, D4, D5, D6, D8, D9, D11, D12, D13, D14, D15, D16, D17, D18, D19, D20, D21, D22, D23, D24, D25, D26, D27, D28, D29, D30, D31, D32, D33, D34, D35, D36, D37: LED; LED_0805_2012Metric
D7: 1N4148WS; D_SOD-323
D10: ESDA25P35; D_1610_4027Metric
J1, J2, J3, J4, J5, J6, J7, J8, J9, J21, J22, J23, J24, J25, J26, J27, J28, J29, J30, J31, J32, J33, J34, J35, J36, J37, J38, J39, J40, J41, J42, J43, J44: IPEX-1; BWIPX-1-001E
J10, J11, J13, J15: Conn_01x03_Pin; PinHeader_1x03_P1.00mm_Vertical_SMD_Pin1Left
J12: Conn_01x10_Pin; PinHeader_1x10_P1.00mm_Vertical_SMD_Pin1Left
J14: Conn_01x02_Pin; PinHeader_1x02_P1.00mm_Vertical_SMD_Pin1Left
J16, J18: Micro_SD_Card_Det1; microSD_HC_MSD-4-A
J17: Conn_01x03_Pin; PinHeader_1x03_P2.54mm_Vertical
J19, J20: USB_C_Receptacle_USB2.0_16P; USB_C_Receptacle_GCT_USB4105-xx-A_16P_TopMnt_Horizontal
J45: Conn_01x24_Pin; PinHeader_1x24_P2.54mm_Vertical
JP1, JP2: SolderJumper_2_Open; SolderJumper-2_P1.3mm_Open_RoundedPad1.0x1.5mm
L1, L2, L3: 10uH; L_Changjiang_FXL0630
R1, R2: 49.9R; R_0402_1005Metric
R3, R4, R5, R6, R7, R8, R9, R19, R20, R33, R36, R69, R78, R88: 0R; R_0402_1005Metric
R10, R11, R12, R13, R14, R15, R16, R18, R58, R61, R62, R63, R64, R65, R66, R67, R68, R70, R71, R72, R73, R74, R75, R76, R77, R80, R81, R82, R83, R84, R85, R86, R87: 470R; R_0402_1005Metric
R17: 100R; R_0402_1005Metric
R21, R28, R29, R30, R31, R32, R34, R35, R48, R51, R55, R56, R57: 10k; R_0402_1005Metric
R22, R23: 4.7k; R_0402_1005Metric
R24, R27, R37, R50, R52, R54: 1k; R_0402_1005Metric
R25, R26: 27R; R_0402_1005Metric
R38, R40, R49: 47k; R_0402_1005Metric
R39, R43: 100k; R_0603_1608Metric
R41, R45: 33k; R_0402_1005Metric
R42, R46: 100k; R_0402_1005Metric
R44, R53: 22k; R_0402_1005Metric
R47: 220k; R_0603_1608Metric
R59, R60: 5.1k; R_0402_1005Metric
R89, R90, R96, R97, R101, R102, R103, R104, R107, R108, R114, R115, R117, R118, R119, R120, R124, R125, R131, R132, R133, R134, R135, R136: 49.9R; R_0603_1608Metric
R91, R92, R93, R94, R95, R98, R99, R100, R105, R106, R109, R110, R111, R112, R113, R116, R121, R122, R123, R126, R127, R128, R129, R130: 10R; R_0402_1005Metric
SW1, SW2, SW3, SW4, SW5, SW6: SW_DIP_x03; SW_DIP_SPSTx03_Slide_6.7x9.18mm_W8.61mm_P2.54mm_LowProfile
TP1, TP2, TP3, TP5, TP6, TP11, TP14, TP16, TP18, TP23, TP25, TP27, TP31, TP34, TP36, TP38, TP43, TP45, TP46: TestPoint; TestPoint_Pad_D1.0mm
TP4, TP7, TP8, TP9, TP10, TP12, TP13, TP15, TP17, TP19, TP20, TP21, TP22, TP24, TP26, TP28, TP29, TP30, TP32, TP33, TP35, TP37, TP39, TP40, TP41, TP42, TP44: TestPoint_Alt; TestPoint_Keystone_5015_Micro_Mini
U1: ICE40HX4K-TQ144; TQFP-144_20x20mm_P0.5mm
U2, U11, U12, U13: 74HC244; TSSOP-20_4.4x6.5mm_P0.65mm
U3: W25Q32JVZP; WSON-8-1EP_6x5mm_P1.27mm_EP3.4x4.3mm
U4: RP2040; QFN-56-1EP_7x7mm_P0.4mm_EP3.2x3.2mm
U5, U8, U9: TPS54302; SOT-23-6
U6, U7: TPS7A4701; Texas_RGW0020A_VQFN-20-1EP_5x5mm_P0.65mm_EP3.15x3.15mm_Ther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
U10: CH224K; SSOP-10-1EP_3.9x4.9mm_P1mm_EP2.1x3.3mm
U14, U19: REF5030ID; SOIC-8_3.9x4.9mm_P1.27mm
U15, U16, U18, U20, U21, U23: MCP4728; MSOP-10_3x3mm_P0.5mm
U17, U22: REF5050ID; SOIC-8_3.9x4.9mm_P1.27mm
U24, U29, U34: TXB0108PW; TSSOP-20_4.4x6.5mm_P0.65mm
U25, U26, U27, U28, U30, U31, U32, U33, U35, U36, U37, U38: TLV3502AIDR; SOIC-8_3.9x4.9mm_P1.27mm
Y1: 12 MHz ABM8-272-T3; Crystal_SMD_Abracon_ABM8AIG-4Pin_3.2x2.5mm

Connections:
+1V1: C24.1, C25.1, C33.1, U4.23 (DVDD), U4.45 (VREG_VOUT), U4.50 (DVDD)
+1V2: C12.1, C13.1, C14.1, C15.1, C16.1, C44.2, C45.2, C46.2, L1.2, R17.1, R38.2, U1.27 (VCC), U1.40 (VCC), U1.92 (VCC), U1.111 (VCC)
+3V3: C1.1, C2.1, C3.1, C4.1, C5.1, C6.1, C7.1, C8.1, C9.1, C10.2, C11.2, C17.1, C18.1, C26.1, C27.1, C28.1, C29.1, C30.1, C31.1, C32.1, C34.1, C35.1, C36.1, C37.1, C38.1, C56.2, C57.2, C58.2, C68.2, C69.2, C70.2, C71.2, C72.2, C73.2, C99.1, C103.1, C109.1, D7.2 (A), J16.4 (VDD), J18.4 (VDD), L2.2, R21.1, R22.1, R23.1, R24.2, R28.1, R29.1, R30.1, R31.1, R32.1, R35.1, R42.2, U1.6 (VCCIO_3), U1.30 (VCCIO_3), U1.46 (VCCIO_2), U1.57 (VCCIO_2), U1.72 (VCC_SPI), U1.89 (VCCIO_1), U1.100 (VCCIO_1), U1.123 (VCCIO_0), U1.131 (VCCIO_0), U2.20 (VCC), U3.8 (VCC), U4.1 (IOVDD), U4.10 (IOVDD), U4.22 (IOVDD), U4.33 (IOVDD), U4.42 (IOVDD), U4.43 (ADC_AVDD), U4.44 (VREG_IN), U4.48 (USB_VDD), U4.49 (IOVDD), U11.20 (VCC), U12.20 (VCC), U13.20 (VCC), U24.2 (V_{CCA}), U24.10 (OE), U29.2 (V_{CCA}), U29.10 (OE), U34.2 (V_{CCA}), U34.10 (OE)
+3V3_A: C49.1, SW2.5, SW4.5, SW6.6, U6.1 (OUT), U6.3 (SENSE/FB), U6.20 (OUT)
+5V5_A: C50.1, C74.1, C75.1, C81.1, C82.1, C86.1, C87.1, C93.1, C94.1, SW2.4, SW4.4, SW6.5, U7.1 (OUT), U7.3 (SENSE/FB), U7.20 (OUT), U14.2 (Vin), U17.2 (Vin), U19.2 (Vin), U22.2 (Vin)
+6V: C42.1, C43.2, C47.1, C48.1, C54.1, C55.2, C62.2, C63.2, C64.2, L3.2, R39.1, R43.1, R46.2, U5.3 (VIN), U6.13 (EN), U6.15 (IN), U6.16 (IN), U7.13 (EN), U7.15 (IN), U7.16 (IN), U8.3 (VIN)
+20V: C60.1, C61.2, C65.1, C66.1, D10.1 (K), J19.A4 (VBUS), J19.A9 (VBUS), J19.B4 (VBUS), J19.B9 (VBUS), R47.1, R51.1, R52.1, R53.1, U9.3 (VIN)
/FPGA/ALT_CLK: R4.2, U1.93 (IOR_140_GBIN3)
/FPGA/BNC_0: R1.2, U1.78 (IOR_114)
/FPGA/BNC_1: R2.2, U1.79 (IOR_115)
/FPGA/CDONE: R30.2, U1.65 (CDONE), U4.17 (GPIO14)
/FPGA/CS: R34.2, U1.71 (IOB_108_SS), U4.28 (GPIO17)
/FPGA/D0: U1.73 (IOR_109), U4.32 (GPIO21)
/FPGA/D1: U1.74 (IOR_110), U4.34 (GPIO22)
/FPGA/D2: U1.75 (IOR_111), U4.35 (GPIO23)
/FPGA/D3: U1.76 (IOR_112), U4.36 (GPIO24)
/FPGA/DEBUG_0: J45.1, U1.1 (IOL_2A), U11.2 (1A0)
/FPGA/DEBUG_1: J45.2, U1.2 (IOL_2B), U11.4 (1A1)
/FPGA/DEBUG_2: J45.3, U1.3 (IOL_3A), U11.6 (1A2)
/FPGA/DEBUG_3: J45.4, U1.4 (IOL_3B), U11.8 (1A3)
/FPGA/DEBUG_4: J45.5, U1.7 (IOL_4A), U11.17 (2A0)
/FPGA/DEBUG_5: J45.6, U1.8 (IOL_4B), U11.15 (2A1)
/FPGA/DEBUG_6: J45.7, U1.9 (IOL_5A), U11.13 (2A2)
/FPGA/DEBUG_7: J45.8, U1.10 (IOL_5B), U11.11 (2A3)
/FPGA/DEBUG_8: J45.9, U1.11 (IOL_8A), U12.2 (1A0)
/FPGA/DEBUG_9: J45.10, U1.12 (IOL_8B), U12.4 (1A1)
/FPGA/DEBUG_10: J45.11, U1.15 (IOL_10A), U12.6 (1A2)
/FPGA/DEBUG_11: J45.12, U1.16 (IOL_10B), U12.8 (1A3)
/FPGA/DEBUG_12: J45.13, U1.17 (IOL_12A), U12.17 (2A0)
/FPGA/DEBUG_13: J45.14, U1.18 (IOL_12B), U12.15 (2A1)
/FPGA/DEBUG_14: J45.15, U1.19 (IOL_13A), U12.13 (2A2)
/FPGA/DEBUG_15: J45.16, U1.22 (IOL_14B), U12.11 (2A3)
/FPGA/DEBUG_16: J45.17, U1.23 (IOL_17A), U13.2 (1A0)
/FPGA/DEBUG_17: J45.18, U1.24 (IOL_17B), U13.4 (1A1)
/FPGA/DEBUG_18: J45.19, U1.25 (IOL_18A), U13.6 (1A2)
/FPGA/DEBUG_19: J45.20, U1.26 (IOL_18B), U13.8 (1A3)
/FPGA/DEBUG_20: J45.21, U1.28 (IOL_23A), U13.17 (2A0)
/FPGA/DEBUG_21: J45.22, U1.29 (IOL_23B), U13.15 (2A1)
/FPGA/DEBUG_22: J45.23, U1.31 (IOL_24A), U13.13 (2A2)
/FPGA/DEBUG_23: J45.24, U1.32 (IOL_24B), U13.11 (2A3)
/FPGA/EXT_CLK: R3.2, U1.38 (IOB_57)
/FPGA/GBIN2: U1.94 (IOR_141_GBIN2), U4.37 (GPIO25)
/FPGA/LED_0: U1.98 (IOR_148), U2.2 (1A0)
/FPGA/LED_1: U1.99 (IOR_152), U2.4 (1A1)
/FPGA/LED_2: U1.101 (IOR_160), U2.6 (1A2)
/FPGA/LED_3: U1.102 (IOR_161), U2.8 (1A3)
/FPGA/LED_4: U1.104 (IOR_164), U2.17 (2A0)
/FPGA/LED_5: U1.105 (IOR_165), U2.15 (2A1)
/FPGA/LED_6: U1.106 (IOR_166), U2.13 (2A2)
/FPGA/LED_7: U1.107 (IOR_167), U2.11 (2A3)
/FPGA/MCU_CLK: U1.37 (IOB_56), U4.39 (GPIO27_ADC1)
/FPGA/PLL_CLK: R5.2, U1.39 (IOB_61)
/FPGA/PLL_LOCK: U1.41 (IOB_63), U4.38 (GPIO26_ADC0)
/FPGA/SCK: U1.70 (IOB_107_SCK), U4.29 (GPIO18)
/FPGA/SI: U1.68 (IOB_106_SDI), U4.30 (GPIO19)
/FPGA/SO: U1.67 (IOB_105_SDO), U4.31 (GPIO20)
/FPGA/TRIG_IN: R8.2, U1.49 (IOB_81_GBIN5)
/FPGA/TRIG_IN_0: U1.110 (IOT_168), U24.9 (A8)
/FPGA/TRIG_IN_1: U1.112 (IOT_169), U24.8 (A7)
/FPGA/TRIG_IN_2: U1.113 (IOT_170), U24.7 (A6)
/FPGA/TRIG_IN_3: U1.114 (IOT_171), U24.6 (A5)
/FPGA/TRIG_IN_4: U1.115 (IOT_172), U24.5 (A4)
/FPGA/TRIG_IN_5: U1.116 (IOT_173), U24.4 (A3)
/FPGA/TRIG_IN_6: U1.117 (IOT_174), U24.3 (A2)
/FPGA/TRIG_IN_7: U1.118 (IOT_177), U24.1 (A1)
/FPGA/TRIG_IN_8: U1.119 (IOT_178), U29.9 (A8)
/FPGA/TRIG_IN_9: U1.120 (IOT_179), U29.8 (A7)
/FPGA/TRIG_IN_10: U1.121 (IOT_181), U29.7 (A6)
/FPGA/TRIG_IN_11: U1.122 (IOT_190), U29.6 (A5)
/FPGA/TRIG_IN_12: U1.124 (IOT_191), U29.5 (A4)
/FPGA/TRIG_IN_13: U1.125 (IOT_192), U29.4 (A3)
/FPGA/TRIG_IN_14: U1.130 (IOT_206), U29.3 (A2)
/FPGA/TRIG_IN_15: U1.134 (IOT_212), U29.1 (A1)
/FPGA/TRIG_IN_16: U1.135 (IOT_213), U34.9 (A8)
/FPGA/TRIG_IN_17: U1.136 (IOT_214), U34.8 (A7)
/FPGA/TRIG_IN_18: U1.137 (IOT_215), U34.7 (A6)
/FPGA/TRIG_IN_19: U1.138 (IOT_216), U34.6 (A5)
/FPGA/TRIG_IN_20: U1.139 (IOT_217), U34.5 (A4)
/FPGA/TRIG_IN_21: U1.141 (IOT_219), U34.4 (A3)
/FPGA/TRIG_IN_22: U1.142 (IOT_220), U34.3 (A2)
/FPGA/TRIG_IN_23: U1.143 (IOT_221), U34.1 (A1)
/FPGA/TRIG_OUT: R9.2, U1.55 (IOB_91)
/FPGA/VETO_IN: R6.2, U1.52 (IOB_82_GBIN4)
/FPGA/VETO_OUT: R7.2, U1.56 (IOB_94)
/FPGA/~CRESET: R31.2, U1.66 (~CRESET), U4.16 (GPIO13)
/FPGA/~INT: R28.2, U1.63 (IOB_103_CBSEL0), U4.27 (GPIO16)
/FPGA/~RESET: R29.2, U1.64 (IOB_104_CBSEL1), U4.18 (GPIO15)
/MCU/CS_A: J16.2 (DAT3/CD), U4.11 (GPIO8)
/MCU/CS_B: J18.2 (DAT3/CD), U4.12 (GPIO9)
/MCU/D+: R25.2, U4.47 (USB_DP)
/MCU/D-: R26.2, U4.46 (USB_DM)
/MCU/DET_A: R33.2, U4.40 (GPIO28_ADC2)
/MCU/DET_B: R36.2, U4.41 (GPIO29_ADC3)
/MCU/QSPI_SCLK: U3.6 (CLK), U4.52 (QSPI_SCLK)
/MCU/QSPI_SD0: U3.5 (DI/IO_{0}), U4.53 (QSPI_SD0)
/MCU/QSPI_SD1: U3.2 (DO/IO_{1}), U4.55 (QSPI_SD1)
/MCU/QSPI_SD2: U3.3 (~WP/IO_{2}), U4.54 (QSPI_SD2)
/MCU/QSPI_SD3: U3.7 (~HOLD/~RESET/IO_{3}), U4.51 (QSPI_SD3)
/MCU/QSPI_SS: R21.2, R27.2, U3.1 (~CS), U4.56 (QSPI_SS)
/MCU/SD_CLK: J16.5 (CLK), J18.5 (CLK), U4.13 (GPIO10)
/MCU/SD_SI: J16.3 (CMD), J18.3 (CMD), U4.14 (GPIO11)
/MCU/SD_SO: J16.7 (DAT0), J18.7 (DAT0), U4.15 (GPIO12)
/MCU/SWCLK: J17.1, U4.24 (SWCLK)
/MCU/SWD: J17.3, U4.25 (SWD)
/MCU/USB_D+: J20.A6 (D+), J20.B6 (D+), R25.1
/MCU/USB_D-: J20.A7 (D-), J20.B7 (D-), R26.1
/MCU/VREF_SCL: R22.2, U4.3 (GPIO1), U15.2 (SCL), U16.2 (SCL), U18.2 (SCL), U20.2 (SCL), U21.2 (SCL), U23.2 (SCL)
/MCU/VREF_SDA: R23.2, U4.2 (GPIO0), U15.3 (SDA), U16.3 (SDA), U18.3 (SDA), U20.3 (SDA), U21.3 (SDA), U23.3 (SDA)
/MCU/XIN: C39.2, U4.20 (XIN), Y1.1
/MCU/XOUT: R37.2, U4.21 (XOUT)
/MCU/~LDAC0: U4.9 (GPIO7), U15.4 (~LDAC)
/MCU/~LDAC1: U4.8 (GPIO6), U16.4 (~LDAC)
/MCU/~LDAC2: U4.7 (GPIO5), U18.4 (~LDAC)
/MCU/~LDAC3: U4.6 (GPIO4), U20.4 (~LDAC)
/MCU/~LDAC4: U4.5 (GPIO3), U21.4 (~LDAC)
/MCU/~LDAC5: U4.4 (GPIO2), U23.4 (~LDAC)
/comparators/COMP_VCC: C98.1, C100.2, C101.2, C102.1, C104.2, C105.2, C106.2, C107.2, C108.1, C110.2, C111.2, C112.1, C113.2, C114.2, C115.2, C116.2, SW6.1, SW6.2, SW6.3, U24.19 (V_{CCB}), U25.8 (V+), U26.8 (V+), U27.8 (V+), U28.8 (V+), U29.19 (V_{CCB}), U30.8 (V+), U31.8 (V+), U32.8 (V+), U33.8 (V+), U34.19 (V_{CCB}), U35.8 (V+), U36.8 (V+), U37.8 (V+), U38.8 (V+)
/comparators/IN0: J21.1 (In), R89.2, U25.2 (-IN_A)
/comparators/IN1: J23.1 (In), R96.2, U25.4 (-IN_B)
/comparators/IN2: J25.1 (In), R101.2, U27.2 (-IN_A)
/comparators/IN3: J27.1 (In), R103.2, U27.4 (-IN_B)
/comparators/IN4: J29.1 (In), R107.2, U30.2 (-IN_A)
/comparators/IN5: J31.1 (In), R114.2, U30.4 (-IN_B)
/comparators/IN6: J33.1 (In), R117.2, U32.2 (-IN_A)
/comparators/IN7: J35.1 (In), R119.2, U32.4 (-IN_B)
/comparators/IN8: J37.1 (In), R124.2, U35.2 (-IN_A)
/comparators/IN9: J39.1 (In), R131.2, U35.4 (-IN_B)
/comparators/IN10: J41.1 (In), R133.2, U37.2 (-IN_A)
/comparators/IN11: J43.1 (In), R135.2, U37.4 (-IN_B)
/comparators/IN12: J22.1 (In), R90.2, U26.2 (-IN_A)
/comparators/IN13: J24.1 (In), R97.2, U26.4 (-IN_B)
/comparators/IN14: J26.1 (In), R102.2, U28.2 (-IN_A)
/comparators/IN15: J28.1 (In), R104.2, U28.4 (-IN_B)
/comparators/IN16: J30.1 (In), R108.2, U31.2 (-IN_A)
/comparators/IN17: J32.1 (In), R115.2, U31.4 (-IN_B)
/comparators/IN18: J34.1 (In), R118.2, U33.2 (-IN_A)
/comparators/IN19: J36.1 (In), R120.2, U33.4 (-IN_B)
/comparators/IN20: J38.1 (In), R125.2, U36.2 (-IN_A)
/comparators/IN21: J40.1 (In), R132.2, U36.4 (-IN_B)
/comparators/IN22: J42.1 (In), R134.2, U38.2 (-IN_A)
/comparators/IN23: J44.1 (In), R136.2, U38.4 (-IN_B)
/comparators/OUT0: R100.1, U25.7 (OUT_A)
/comparators/OUT1: R99.1, U25.6 (OUT_B)
/comparators/OUT2: R98.1, U27.7 (OUT_A)
/comparators/OUT3: R95.1, U27.6 (OUT_B)
/comparators/OUT4: R94.1, U30.7 (OUT_A)
/comparators/OUT5: R93.1, U30.6 (OUT_B)
/comparators/OUT6: R92.1, U32.7 (OUT_A)
/comparators/OUT7: R91.1, U32.6 (OUT_B)
/comparators/OUT8: R116.1, U35.7 (OUT_A)
/comparators/OUT9: R113.1, U35.6 (OUT_B)
/comparators/OUT10: R112.1, U37.7 (OUT_A)
/comparators/OUT11: R111.1, U37.6 (OUT_B)
/comparators/OUT12: R110.1, U26.7 (OUT_A)
/comparators/OUT13: R109.1, U26.6 (OUT_B)
/comparators/OUT14: R106.1, U28.7 (OUT_A)
/comparators/OUT15: R105.1, U28.6 (OUT_B)
/comparators/OUT16: R130.1, U31.7 (OUT_A)
/comparators/OUT17: R129.1, U31.6 (OUT_B)
/comparators/OUT18: R128.1, U33.7 (OUT_A)
/comparators/OUT19: R127.1, U33.6 (OUT_B)
/comparators/OUT20: R126.1, U36.7 (OUT_A)
/comparators/OUT21: R123.1, U36.6 (OUT_B)
/comparators/OUT22: R122.1, U38.7 (OUT_A)
/comparators/OUT23: R121.1, U38.6 (OUT_B)
/comparators/VREF0: TP7.1, U15.6 (VOUTA), U25.1 (+IN_A)
/comparators/VREF1: TP8.1, U15.7 (VOUTB), U25.3 (+IN_B)
/comparators/VREF2: TP9.1, U15.8 (VOUTC), U27.1 (+IN_A)
/comparators/VREF3: TP10.1, U15.9 (VOUTD), U27.3 (+IN_B)
/comparators/VREF4: TP12.1, U16.6 (VOUTA), U30.1 (+IN_A)
/comparators/VREF5: TP13.1, U16.7 (VOUTB), U30.3 (+IN_B)
/comparators/VREF6: TP15.1, U16.8 (VOUTC), U32.1 (+IN_A)
/comparators/VREF7: TP17.1, U16.9 (VOUTD), U32.3 (+IN_B)
/comparators/VREF8: TP19.1, U18.6 (VOUTA), U35.1 (+IN_A)
/comparators/VREF9: TP20.1, U18.7 (VOUTB), U35.3 (+IN_B)
/comparators/VREF10: TP21.1, U18.8 (VOUTC), U37.1 (+IN_A)
/comparators/VREF11: TP22.1, U18.9 (VOUTD), U37.3 (+IN_B)
/comparators/VREF12: TP26.1, U20.6 (VOUTA), U26.1 (+IN_A)
/comparators/VREF13: TP28.1, U20.7 (VOUTB), U26.3 (+IN_B)
/comparators/VREF14: TP29.1, U20.8 (VOUTC), U28.1 (+IN_A)
/comparators/VREF15: TP30.1, U20.9 (VOUTD), U28.3 (+IN_B)
/comparators/VREF16: TP32.1, U21.6 (VOUTA), U31.1 (+IN_A)
/comparators/VREF17: TP33.1, U21.7 (VOUTB), U31.3 (+IN_B)
/comparators/VREF18: TP35.1, U21.8 (VOUTC), U33.1 (+IN_A)
/comparators/VREF19: TP37.1, U21.9 (VOUTD), U33.3 (+IN_B)
/comparators/VREF20: TP39.1, U23.6 (VOUTA), U36.1 (+IN_A)
/comparators/VREF21: TP40.1, U23.7 (VOUTB), U36.3 (+IN_B)
/comparators/VREF22: TP41.1, U23.8 (VOUTC), U38.1 (+IN_A)
/comparators/VREF23: TP42.1, U23.9 (VOUTD), U38.3 (+IN_B)
/dac/VREF_A: C76.1, C77.1, C79.1, C80.1, C84.1, C85.1, SW2.1, SW2.2, SW2.3, TP4.1, U15.1 (VDD), U16.1 (VDD), U18.1 (VDD)
/dac/VREF_A_3V: C78.1, SW3.6, U14.6 (Vout)
/dac/VREF_A_5V: C83.1, SW3.5, U17.6 (Vout)
/dac/VREF_B: C88.1, C89.1, C91.1, C92.1, C96.1, C97.1, SW4.1, SW4.2, SW4.3, TP24.1, U20.1 (VDD), U21.1 (VDD), U23.1 (VDD)
/dac/VREF_B_3V: C90.1, SW5.6, U19.6 (Vout)
/dac/VREF_B_5V: C95.1, SW5.5, U22.6 (Vout)
/dac/VREF_SELECT_A: SW2.6, SW3.1, SW3.2, SW3.3, SW5.4
/dac/VREF_SELECT_B: SW3.4, SW4.6, SW5.1, SW5.2, SW5.3
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

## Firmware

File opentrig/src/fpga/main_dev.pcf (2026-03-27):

set_io mcu_clk 37       # GPIO27
#set_io ext_clk 38               # External clock
        set_io ext_clk 44        # Internal clock from SIM PICO

set_io pll_clk 39
set_io pll_lock 41      # GPIO26

set_io t_zero_received 73

set_io spi_clk 70
set_io spi_cs 71
set_io spi_si 68
set_io spi_so 67

set_io veto_in 52
set_io trig_in 49
set_io trig_id 93
        #set_io veto_in 21
        #set_io trig_in 20
        #set_io trig_id 42

set_io trig_out 55
set_io veto_out 56

set_io global_reset 94
set_io mem_swap_interrupt 64


# mcu connections

set_io interrupt 63
set_io reset 64

# inputs
set_io c_input[0] 1
set_io c_input[1] 2
set_io c_input[2] 3
set_io c_input[3] 4
set_io c_input[4] 7
set_io c_input[5] 8
set_io c_input[6] 9
set_io c_input[7] 10
set_io c_input[8] 11
set_io c_input[9] 12
set_io c_input[10] 15
set_io c_input[11] 16
set_io c_input[12] 17
set_io c_input[13] 18
set_io c_input[14] 19
set_io c_input[15] 22
set_io c_input[16] 23
set_io c_input[17] 24
set_io c_input[18] 25
set_io c_input[19] 26
set_io c_input[20] 28
set_io c_input[21] 29
set_io c_input[22] 31
set_io c_input[23] 32

# led
set_io led[0] 98
set_io led[1] 99
set_io led[2] 101
set_io led[3] 102
set_io led[4] 104
set_io led[5] 105
set_io led[6] 106
set_io led[7] 107


# debug outputs
set_io aux_out[0] 80
set_io aux_out[1] 81
set_io aux_out[2] 82
set_io aux_out[3] 83
set_io aux_out[4] 84
set_io aux_out[5] 85
set_io aux_out[6] 87
set_io aux_out[7] 88
set_io aux_out[8] 90
set_io aux_out[9] 91

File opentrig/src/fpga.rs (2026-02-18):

use defmt::*;
use embassy_rp::{
    gpio::{AnyPin, Input, Level, Output, Pull},
    pwm::{Config as PWMConfig, Pwm, SetDutyCycle},
    spi::{Async, Config as SPIConfig, Instance, Phase, Polarity, Spi},
};
use embassy_time::Timer;

pub struct DAQFpga<'a, T>
where
    T: Instance,
{
    spi: Spi<'a, T, Async>,

    cs: Output<'a>,
    creset: Output<'a>,
    cdone: Input<'a>,

    mcu_clk: Pwm<'a>,
    pll_lock: Input<'a>,

    reset_pin: Output<'a>,
    interrupt: Input<'a>,

    read_buffer: [u8; 16],
}

pub fn daq_fpga_spi_config() -> SPIConfig {
    let mut config = SPIConfig::default();
    config.frequency = 5_000_000;
    config.polarity = Polarity::IdleHigh;
    config.phase = Phase::CaptureOnSecondTransition;
    config
}

pub fn daq_fpga_clock_config() -> PWMConfig {
    let clock_freq_hz = embassy_rp::clocks::clk_sys_freq();
    let divider = 1u8;
    let period = (clock_freq_hz / (10_000_000 * divider as u32)) as u16 - 1;

    let mut c = PWMConfig::default();
    c.top = period;
    c.divider = divider.into();

    c
}

impl<'a, T> DAQFpga<'a, T>
where
    T: Instance,
{
    pub fn new(
        spi_bus: Spi<'a, T, Async>,

        cs: AnyPin,
        creset: AnyPin,
        cdone: AnyPin,

        mcu_clk: Pwm<'a>,
        pll_lock: AnyPin,

        reset_pin: AnyPin,
        interrupt: AnyPin,
    ) -> Self {
        Self {
            spi: spi_bus,

            cs: Output::new(cs, Level::Low),
            creset: Output::new(creset, Level::Low),
            cdone: Input::new(cdone, Pull::None),

            mcu_clk: mcu_clk,
            pll_lock: Input::new(pll_lock, Pull::Down),

            reset_pin: Output::new(reset_pin, Level::High),
            interrupt: Input::new(interrupt, Pull::None),

            read_buffer: [0u8; 16],
        }
    }

    pub async fn configure(&mut self, bitstream: &'static [u8]) -> Result<(), ()> {
        if self.cdone.is_low() {
            info!("config proceed");
        } else {
            info!("config err, cdone already high");
            return Err(());
        }

        self.creset.set_high();
        Timer::after_micros(1200).await;

        self.cs.set_high();
        self.spi.write(&[0]).await.map_err(|_| ())?;
        info!("ok 8 dummy");
        self.cs.set_low();

        info!("bitstream size: {}", bitstream.len());
        self.spi.write(bitstream).await.map_err(|_| ())?;
        info!("ok bitstream");
        self.cs.set_high();

        if self.cdone.is_high() {
            info!("last 49(56) cycles");
            self.spi.write(&[0xFFu8; 7]).await.map_err(|_| ())?;
            info!("last config 56 bits ok");
            info!("confirm config done");
        } else {
            warn!("cdone never high");
            return Err(());
        }

        Ok(())
    }

    pub async fn setup_clocks(&mut self) -> Result<(), ()> {
        self.mcu_clk.set_duty_cycle_percent(50).map_err(|_| ())?;

        while self.pll_lock.is_low() {
            warn!("pll not locked");
            Timer::after_millis(500).await;
        }
        info!("pll locked");

        Ok(())
    }

    pub fn reset(&mut self) -> Result<(), ()> {
        self.reset_pin.set_low();
        self.reset_pin.set_high();

        match self.interrupt.is_low() {
            true => {
                info!("reset success");
                Ok(())
            }
            false => {
                warn!("reset failed");
                Err(())
            }
        }
    }

    pub async fn await_sample(&mut self) {
        self.interrupt.wait_for_falling_edge().await;
    }

    pub fn last_sample_bytes(& self) -> &[u8; 16] {
        &self.read_buffer
    }

    // pub fn read_sample(&mut self) -> Result<DAQSample, ()> {
    pub fn read_sample(&mut self) {
        self.cs.set_low();
        self.spi
            .blocking_read(&mut self.read_buffer)
            .map_err(|_| ()).unwrap();
        self.cs.set_high();
    }
}

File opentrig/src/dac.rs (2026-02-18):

//! This module is meant to manage 6 MCP4728 DACs that share a common I2C line,
//! using the mcp4728 crate.
//!
//! Some functionalities are left to be handled by the mcp4728 crate itself:
//! Functions like MCP4728Async.fast_write() are not cloned in this module, users
//! should access the MCP4728Async instances whithin the DacManager.dacs field.

use defmt::*;
use embassy_embedded_hal::shared_bus::{I2cDeviceError, asynch::i2c::I2cDevice};
use embassy_rp::bind_interrupts;
use embassy_rp::gpio::Output;
use embassy_rp::i2c::{self, I2c, InterruptHandler};
use embassy_rp::peripherals::I2C0;
use embassy_sync::blocking_mutex::raw::NoopRawMutex;
use embassy_sync::mutex::Mutex;
use mcp4728::{GainMode, MCP4728Async, PowerDownMode, Registers};
use static_cell::StaticCell;
use {defmt_rtt as _, panic_probe as _};

/// Error returned by DacManager.
#[derive(Debug)]
pub enum DacError {
    InvalidDacId(usize),
    InputVoltageOutOfBounds(u16),
    McpError(mcp4728::Error<I2cDeviceError<embassy_rp::i2c::Error>>),
}

bind_interrupts!(struct Irqs {
    I2C0_IRQ => InterruptHandler<I2C0>;
});

/// Returns a static initialized I2c bus wrapped in a Mutex.
fn init_i2c(
    i2c_peri: I2C0,
    scl: impl i2c::SclPin<I2C0>,
    sda: impl i2c::SdaPin<I2C0>,
) -> &'static Mutex<NoopRawMutex, I2c<'static, I2C0, i2c::Async>> {
    // Initialize bus.
    let i2c = I2c::new_async(i2c_peri, scl, sda, Irqs, i2c::Config::default());

    // Wrap bus.
    static I2C_BUS: StaticCell<Mutex<NoopRawMutex, I2c<'static, I2C0, i2c::Async>>> =
        StaticCell::new();
    I2C_BUS.init(Mutex::new(i2c))
}

/// Manager for 6 MCP4728 DACs.
pub struct DacManager<'a> {
    pub dacs: [MCP4728Async<I2cDevice<'a, NoopRawMutex, I2c<'static, I2C0, i2c::Async>>>; 6],
    pub ldacs: [Output<'a>; 6],
}

impl<'a> DacManager<'a> {
    /// Create a new DacManager instance.
    pub fn new(
        i2c_peri: I2C0,
        scl: impl i2c::SclPin<I2C0>,
        sda: impl i2c::SdaPin<I2C0>,
        ldacs: [Output<'a>; 6],
    ) -> Self {
        let i2c_bus = init_i2c(i2c_peri, scl, sda);

        Self {
            dacs: [
                MCP4728Async::new(I2cDevice::new(i2c_bus), 0x60),
                MCP4728Async::new(I2cDevice::new(i2c_bus), 0x61),
                MCP4728Async::new(I2cDevice::new(i2c_bus), 0x62),
                MCP4728Async::new(I2cDevice::new(i2c_bus), 0x63),
                MCP4728Async::new(I2cDevice::new(i2c_bus), 0x64),
                MCP4728Async::new(I2cDevice::new(i2c_bus), 0x65),
            ],
            ldacs: ldacs,
        }
    }

    /// Set all DACs to their default vref, gain and powerdown modes.
    pub async fn init(&mut self) -> Result<(), DacError> {
        // Get default values.
        let vref = mcp4728::VoltageReferenceMode::Internal;
        let gain = GainMode::TimesOne;
        let power = PowerDownMode::Normal;

        // Loop through DACs to write defaults.
        for i in 0..6 {
            self.dacs[i]
                .write_voltage_reference_mode(vref, vref, vref, vref)
                .await
                .map_err(|e| DacError::McpError(e))
                .unwrap();
            self.dacs[i]
                .write_gain_mode(gain, gain, gain, gain)
                .await
                .map_err(|e| DacError::McpError(e))
                .unwrap();
            self.dacs[i]
                .write_power_down_mode(power, power, power, power)
                .await
                .map_err(|e| DacError::McpError(e))
                .unwrap();
        }

        info!("All MCPs set to default modes.");

        Ok(())
    }

    /// Get the DAC corresponding to a specific ID.
    pub async fn get_dac(
        &mut self,
        dac_id: usize,
    ) -> Result<
        &mut MCP4728Async<I2cDevice<'a, NoopRawMutex, I2c<'static, I2C0, i2c::Async>>>,
        DacError,
    > {
        // Handle ValueOutOfBounds error.
        if dac_id > 5 {
            return Err(DacError::InvalidDacId(dac_id));
        }
        Ok(&mut self.dacs[dac_id])
    }

    /// Read the data from the specified MCP4728 on the specified channel.
    pub async fn read_channel(
        &mut self,
        dac_id: usize,
        channel: mcp4728::Channel,
    ) -> Result<mcp4728::ChannelState, DacError> {
        // Read the registers of the correct DAC.
        let dac = self.get_dac(dac_id).await.unwrap();
        let registers: Registers = dac.read().await.map_err(|e| DacError::McpError(e)).unwrap();

        // Return the specified channel.
        Ok(match channel {
            mcp4728::Channel::A => registers.channel_a_input.channel_state,
            mcp4728::Channel::B => registers.channel_b_input.channel_state,
            mcp4728::Channel::C => registers.channel_c_input.channel_state,
            mcp4728::Channel::D => registers.channel_d_input.channel_state,
        })
    }

    /// Change the voltage on a single channel to the specified value in mv.
    pub async fn set_voltage(
        &mut self,
        dac_id: usize,
        channel: mcp4728::Channel,
        voltage: u16,
    ) -> Result<(), DacError> {
        let channel_state = self.read_channel(dac_id, channel).await.unwrap();
        let gain_mode = channel_state.gain_mode;
        let input = match gain_mode {
            GainMode::TimesOne => voltage * 2,
            GainMode::TimesTwo => voltage,
        };

        if input > 4096 {
            return Err(DacError::InputVoltageOutOfBounds(input));
        }

        // Create the new data.
        let mut channel_state = self.read_channel(dac_id, channel).await.unwrap().clone();
        channel_state.value = input;

        // Get referenced DAC.
        let dac = self.get_dac(dac_id).await.unwrap();

        // Write the data.
        dac.single_write(channel, mcp4728::OutputEnableMode::Update, &channel_state)
            .await
            .map_err(|e| DacError::McpError(e))
            .unwrap();

        info!("Voltage changed successfully.");
        Ok(())
    }

    /// Change the voltage reference mode on a single channel.
    pub async fn set_vref_mode(
        &mut self,
        dac_id: usize,
        channel: mcp4728::Channel,
        mode: mcp4728::VoltageReferenceMode,
    ) -> Result<(), DacError> {
        // Create the new data.
        let mut channel_state = self.read_channel(dac_id, channel).await.unwrap().clone();
        channel_state.voltage_reference_mode = mode;

        // Get referenced DAC.
        let dac = self.get_dac(dac_id).await.unwrap();

        // Write the data.
        dac.single_write(channel, mcp4728::OutputEnableMode::Update, &channel_state)
            .await
            .map_err(|e| DacError::McpError(e))
            .unwrap();

        info!("Vref mode changed successfully.");
        Ok(())
    }

    /// Change the gain mode on a single channel.
    pub async fn set_gain_mode(
        &mut self,
        dac_id: usize,
        channel: mcp4728::Channel,
        mode: mcp4728::GainMode,
    ) -> Result<(), DacError> {
        // Create the new data.
        let mut channel_state = self.read_channel(dac_id, channel).await.unwrap().clone();
        channel_state.gain_mode = mode;

        // Get referenced DAC.
        let dac = self.get_dac(dac_id).await.unwrap();

        // Write the data.
        dac.single_write(channel, mcp4728::OutputEnableMode::Update, &channel_state)
            .await
            .map_err(|e| DacError::McpError(e))
            .unwrap();

        info!("Gain mode changed successfully.");
        Ok(())
    }

    /// Change the gain mode on a single channel.
    pub async fn set_power_down_mode(
        &mut self,
        dac_id: usize,
        channel: mcp4728::Channel,
        mode: mcp4728::PowerDownMode,
    ) -> Result<(), DacError> {
        // Create the new data.
        let mut channel_state = self.read_channel(dac_id, channel).await.unwrap().clone();
        channel_state.power_down_mode = mode;

        // Get referenced DAC.
        let dac = self.get_dac(dac_id).await.unwrap();

        // Write the data.
        dac.single_write(channel, mcp4728::OutputEnableMode::Update, &channel_state)
            .await
            .map_err(|e| DacError::McpError(e))
            .unwrap();

        info!("Power down mode changed successfully.");
        Ok(())
    }

    /// Change the voltage on all 24 channels to the specified value in mv.
    pub async fn set_all_voltages(&mut self, voltages: [u16; 24]) -> Result<(), DacError> {
        // Loop through each DAC.
        for i in 0..6 {
            let j = i * 4;

            // Read the gain mode of each channel.
            let registers = self.dacs[i]
                .read()
                .await
                .map_err(|e| DacError::McpError(e))
                .unwrap();
            let gains = [
                registers.channel_a_input.channel_state.gain_mode,
                registers.channel_b_input.channel_state.gain_mode,
                registers.channel_c_input.channel_state.gain_mode,
                registers.channel_d_input.channel_state.gain_mode,
            ];
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

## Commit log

2025-06-30 Added the DAC/ADC array for analog conversion.
    Added an array of 6 quad-channels DAC with I2C interface to control the threshold voltage of a set of 12 dual channel ADCs. Loose, general wiring of FPGA and MCU present, detailed schematics in the w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
    [converters.kicad_sch, digital.kicad_pcb, digital.kicad_sch, fpga.kicad_sch]
2025-07-02 Added SD card readers and USB-C for power in.
    [converters.kicad_sch, converters2.kicad_sch, digital.kicad_sch, fpga.kicad_sch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]
2025-07-03 generate pdfs
    [digital.kicad_sch]
2025-07-09 Small aesthetic changes and small rework of power sheet.
    [converters.kicad_sch, digital.kicad_sch, fpga.kicad_sch, power.kicad_sch]
2025-07-09 add power redundancy with OR-ing controller
    [power.kicad_sch]
2025-07-10 complete power
    [digital.kicad_sch, power.kicad_sch, power_sipm.kicad_sch, usb.kicad_sch]
2025-07-11 reroute dac + comparators
    [comparators.kicad_sch, dac.kicad_sch, digital.kicad_sch, mcu.kicad_sch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]
2025-07-11 series resistors
    [comparators.kicad_sch, dac.kicad_sch, power_sipm.kicad_sch, usb.kicad_sch]
2025-07-11 annotate dip switches
    [comparators.kicad_sch, dac.kicad_sch, power_sipm.kicad_sch, usb.kicad_sch]
2025-07-16 complete schematic wiring
    [comparators.kicad_sch, dac.kicad_sch, debug.kicad_sch, digital.kicad_sch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]
2025-07-17 update power system + add LCSC part numbers
    [comparators.kicad_sch, dac.kicad_sch, debug.kicad_sch, digital.kicad_sch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]
2025-07-17 apply manufacturing BOM
    [comparators.kicad_sch, dac.kicad_sch, debug.kicad_sch, digital.kicad_sch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]
2025-07-18 route digital inputs
    [comparators.kicad_sch, digital.kicad_pcb, digital.kicad_sch, power_sipm.kicad_sch]
2025-07-18 route power
    [digital.kicad_pcb]
2025-07-18 route more
    [comparators.kicad_sch, dac.kicad_sch, debug.kicad_sch, digital.kicad_pcb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]
2025-07-18 route mcu
    [digital.kicad_pcb, digital.kicad_sch, fpga.kicad_sch, mcu.kicad_sch]
2025-07-19 wire until sipm power
    [debug.kicad_sch, digital.kicad_pcb, fpga.kicad_sch, mcu.kicad_sch]
2025-07-20 route all signal
    [debug.kicad_sch, digital.kicad_pcb, digital.kicad_sch, fpga.kicad_sch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]
2025-07-20 add board edge
    [digital.kicad_pcb]
2025-07-21 finish pcb
    [digital.kicad_sch, mcu.kicad_sch]
2025-08-02 add trig id pin
2025-09-16 Added default MCP voltage setting to the minimal example.
2025-11-09 add picture of bare PCB
